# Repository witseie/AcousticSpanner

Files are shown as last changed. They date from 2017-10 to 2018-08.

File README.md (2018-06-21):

# DIY Acoustic Spanner

## Credits
* Ermes Toninelli, Mitchell A. Cox, Graham M. Gibson, Stuart D. Brown, Matthew P. Edgar, Andrew Forbes, Miles J. Padgett 
(Andrew.Forbes@wits.ac.za; Miles.Padgett@glasgow.ac.uk)

## Acknowledgements
* University of Glasgow, Scotland, United Kingdom
* University of the Witwatersrand, Johannesburg, South Africa
* EPSRC
* Centre for doctoral training in Intelligent Sensing and Measurment

## Introduction

Waves are ubiquitous in nature and we are all familiar with them: think water waves, light waves, sound waves, and so on. Everyone is familiar with the force that waves can impart on objects placed in their path. For example, a laser pointer shining on an object exerts a force on it, albeit a very small one. As it turns out, this force is directly proportional to the power of the wave and inversely proportional to its group velocity: that is, for the same power, a slower wave can exert a bigger force than a faster wave. Therefore, in the case of light waves the force is very small, as the speed of light is a very big number. Conversely, for the much slower sound waves (sound is approximately one million times slower than light) it is possible to exert a much bigger force, for an equal power expenditure.

In addition to linear momentum, both light and sound can carry orbital angular momentum (OAM). Whereas linear momentum allows one to ‘push’ objects along the direction of propagation, OAM can be used to rotate them! This form of momentum is different from the perhaps more familiar spin angular momentum, which gives rise to the phenomenon of polarisation, and it can be visualised, in the case of light, as each photon spinning on itself. When an OAM carrying field interacts with an object, it exerts a force both along the direction of propagation and around it: like the sort of force that is required to open a door, by both turning the door knob and by pushing the door.

Another example of the difference between spin angular momentum and orbital angular momentum is the Earth and Moon. The Earth rotates about it's own axis and thus has spin angular momentum. The Moon orbits around the Earth and thus has orbital angular momentum!

OAM arises from a phase structure within the field. Accordingly, many waves are used to create a certain field and the phase differences between these waves can be engineered by introducing delays, often referred to as a phased array. For example, if the waves are in phase with each other (i.e. without delays) the field can be visualised as a series of plane waves, for which the intensity of the waves is the same all over. If however, the phases are regularly changed from 0 to 2pi (one full cycle) in an azimuthal manner (going around the direction of propagation), then the field takes the form of a spiral. This is the type of field that gives rise to OAM.

In this work we use OAM carrying sound waves to build an acoustic spanner. An acoustic spanner allows to exert orbital angular momentum (OAM) on objects, causing them to rotate. Seeing this phenomenon in action is an excellent opportunity to think about the exchange of energy between sound waves and matter, and it is hence an important pedagogical tool. However, building an acoustic spanner able to spin macroscopic objects can require relatively expensive equipment and advanced technical skills. We show how to build a free-space acoustic spanner based on a 3D-printed sound-guiding structure and common electrical components. We show a video of our free-space acoustic spanner in action, in which a styrofoam packing peanut spins in a circular motion and changes direction according to the handedness of the OAM sound (see attached video).

## How do I build one?

1. You will need to get a PCB manufactured. Gerbers are provided which you can send through to your favourite manufacturer. We use Elecrow because they are cheap, fast and do a good job.
2. Accumulate all the compoments. A Bill Of Materials (BOM) is provided as a spreadsheet. The total cost is less than $100.
3. Learn to solder if you don't already know how (YouTube?). Solder all the components, carefully, to the PCB. 
4. Check your soldering and that each component is in the right place. Also check for solder bridges that shouldn't be there.
5. Burn the provided firmware to an Arduino Due using the Arduino IDE or Visual Studio Code.
6. Plug everything together and turn it on! You need to connect a 12V, 1A (or more) power supply to the top PCB for this to work.

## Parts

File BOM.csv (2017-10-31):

Qty | Value | Device | Package | Parts | Description
4 | Optional | AUDIO-JACKPTH | AUDIO-JACK | JP1 | JP2 | JP4 | JP5 | 3.5mm Audio Jack
4 |  | LED5MM | LED5MM | LED1 | LED2 | LED3 | LED4 | LED
1 | Pin Header | M03LOCK | 1X03_LOCK | JP3 | Header 3
17 | Screw Terminal | W237-102 | W237-102 | X1 | X2 | X3 | X4 | X5 | X6 | X7 | X8 | X9 | X10 | X11 | X12 | X13 | X14 | X15 | X16 | X17 | WAGO SCREW CLAMP
1 | 0.1u | C-EU025-025X050 | C025-025X050 | C27 | CAPACITOR | European symbol
10 | 1000u | CPOL-EUE5-10.5 | E5-10 | 5 | C25 | C29 | C30 | C32 | C33 | C37 | C40 | C41 | C43 | C44 | POLARIZED CAPACITOR | European symbol
11 | 100n | C-EU025-025X050 | C025-025X050 | C26 | C28 | C31 | C34 | C36 | C38 | C39 | C42 | C45 | C47 | C48 | CAPACITOR | European symbol
8 | 100nF | C-EU025-025X050 | C025-025X050 | C2 | C5 | C8 | C11 | C14 | C17 | C20 | C23 | CAPACITOR | European symbol
1 | 10k | R-EU_0207/2V | 0207/2V | R 17 | RESISTOR | European symbol
1 | 1N5400 | 1N5400 | DO201-15 | D1 | DIODE
5 | 1k | R-EU_0207/2V | 0207/2V | R 18 | R 19 | R 20 | R 21 | R 22 | RESISTOR | European symbol
16 | 270 1% | R-EU_0207/2V | 0207/2V | R 1 | R 2 | R 3 | R 4 | R 5 | R 6 | R 7 | R 8 | R 9 | R 10 | R 11 | R 12 | R 13 | R 14 | R 15 | R 16 | RESISTOR | European symbol
16 | 4.7mH 5% | L-US0207/2V | 0207/2V | L1 | L2 | L3 | L4 | L5 | L6 | L7 | L8 | L9 | L10 | L11 | L12 | L13 | L14 | L15 | L16 | INDUCTOR | American symbol
16 | 47nF | C-EU025-025X050 | C025-025X050 | C1 | C3 | C4 | C6 | C7 | C9 | C10 | C12 | C13 | C15 | C16 | C18 | C19 | C21 | C22 | C24 | CAPACITOR | European symbol
2 | 47u | CPOL-EUE2.5-5 | E2 | 05-May | C35 | C46 | POLARIZED CAPACITOR | European symbol
1 | Arduino Due | Arduino Due | Arduino Due | B1
1 | POWER_JACKSLT | POWER_JACKSLT | POWER_JACK_SLOT | JP6 | Power Jack
2 | TDA7375V | TDA7375V | MULTIWATT-15V | IC1 | IC2
1 | TOGGLE | SWITCH-MOMENTARY-2PTH | TACTILE-PTH | S1 | Various NO switches- pushbuttons | reed | etc

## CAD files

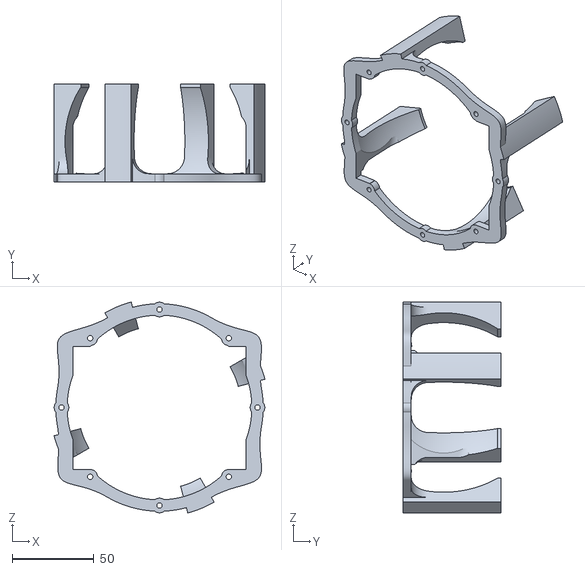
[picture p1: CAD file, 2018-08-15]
Hardware/3D printing/supportStructure.stl
129.4 x 60.0 x 129.4

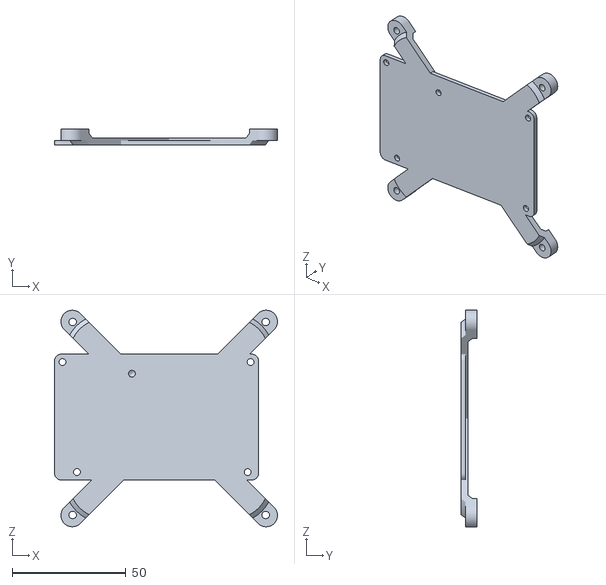
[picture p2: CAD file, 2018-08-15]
Hardware/3D printing/conesToArduinoConnectingStructure.stl
97.9 x 7.00 x 95.0

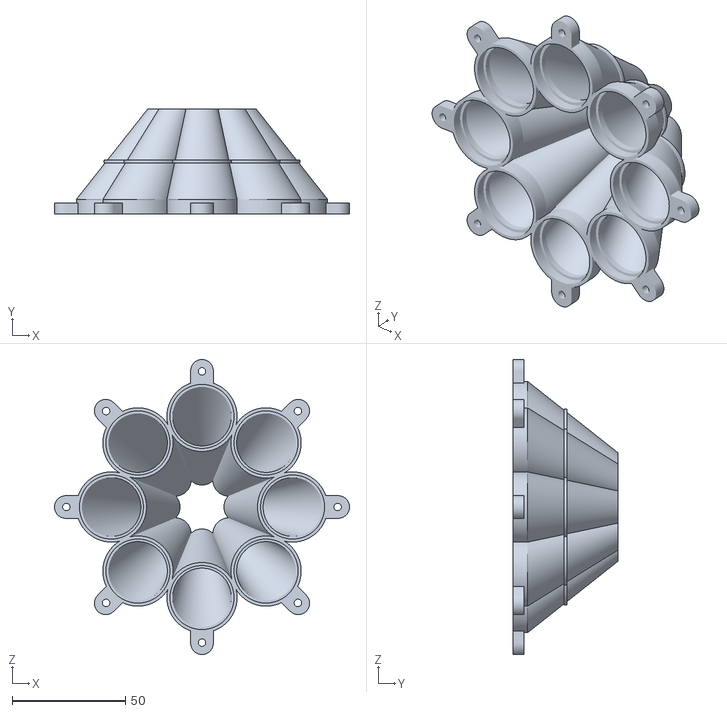
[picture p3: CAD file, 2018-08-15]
Hardware/3D printing/acousticConcentrator.stl
130.2 x 46.5 x 130.2

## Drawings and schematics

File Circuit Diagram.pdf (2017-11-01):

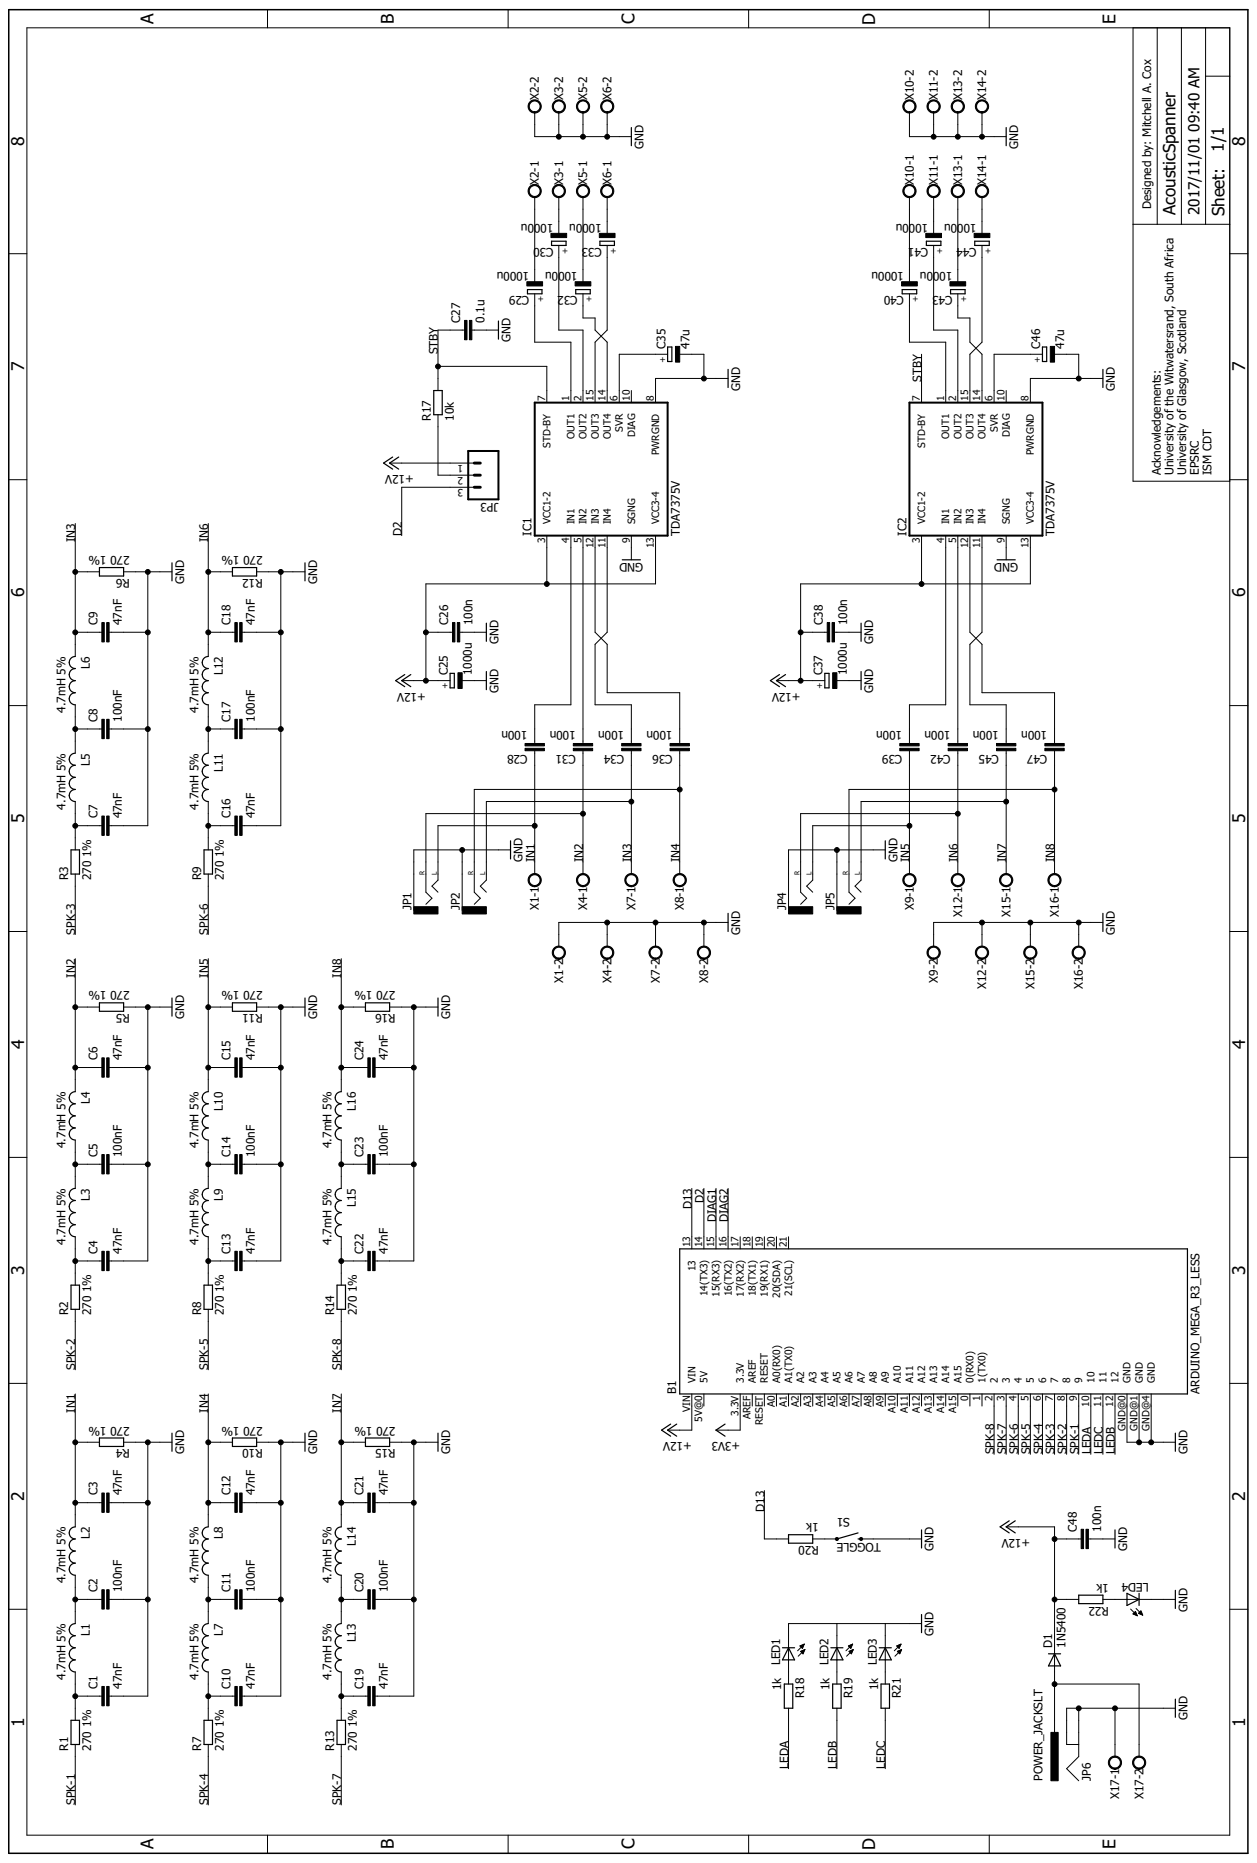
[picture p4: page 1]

Designed by: Mitchell A. Cox Acknowledgements: University of the Witwatersrand, South Africa University of Glasgow, Scotland EPSRC

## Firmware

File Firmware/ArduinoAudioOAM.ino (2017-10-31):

/*
 * ArduinoAudioOAM by Mitchell A. Cox (mitchell.cox@wits.ac.za)
 * https://github.com/witseie/ArduinoAudioOAM
 * MIT License
 * 
 * Designed to go with hardware: https://github.com/witseie/MegaSineShield
 * 
 * This code is written for the Arduino Due. 
 * 8 PWMs are used to generate sine waves pi/4 out of phase with each other.
 * When these signals are amplified and the speakers placed correctly, a
 * wavefront with orbital angular momentum is generated which can apply a
 * torque to an object.
 * 
 * Hardware Interfaces:
 * A button is present which switches the OAM \ell=+-1
 * Three LEDs present a rotation animation to represent \ell=+-1
 * 
 * 
 * References:
 * http://www.analog.com/media/en/training-seminars/tutorials/MT-085.pdf
 * http://interface.khm.de/index.php/lab/interfaces-advanced/arduino-dds-sinewave-generator/
 * 
 */

// Tweakable Parameters:
#define SINE_FREQUENCY 50 //Hz
#define NUM_OUTPUTS 8
#define OAM_l 1
#define PWM_FREQ 32812.5 //Hz (VARIANT_MCK/128/20)

#define SPK1 2
#define SPK2 3
#define SPK3 4
#define SPK4 5
#define SPK5 6
#define SPK6 7
#define SPK7 8
#define SPK8 9

#define BTN_PIN 13
#define LED1_PIN 10
#define LED2_PIN 11
#define LED3_PIN 12

#define DEBOUNCE_DELAY 50 //ms

// For the direction LEDs
#define LED_DELAY_MS 100 //ms

// Calculated / Fixed Parameters:
#define PHASE_SHIFT 2 * PI *OAM_l / NUM_OUTPUTS
#define PI_OVER_255 PI / 255

// Redefine internal Arduino stuff for analogWrite to use more than 1kHz freq.
#undef TC_FREQUENCY
#define TC_FREQUENCY PWM_FREQ
#undef PWM_FREQUENCY
#define PWM_FREQUENCY PWM_FREQ

/*
* Global Variables ------------------------------------------------------------
*/
// Lookup table for sine wave
uint8_t sine256[256];

const double refClk = PWM_FREQ;

double freq;

volatile uint8_t offset;
volatile uint32_t phaseAccum;
volatile uint32_t phaseShift[NUM_OUTPUTS];
volatile uint32_t tuningWord;

bool direction = true; //true = +, false = -

uint8_t whichLED = 1; //which LED is on (1,2 or 3)

/*
* Utility Functions -----------------------------------------------------------
*/

void startTimer(Tc *tc, uint32_t channel, IRQn_Type irq, uint32_t frequency)
{
  //See https://forum.arduino.cc/index.php?topic=130423.0
  pmc_set_writeprotect(false);
  pmc_enable_periph_clk((uint32_t)irq);
  TC_Configure(tc, channel, TC_CMR_WAVE | TC_CMR_WAVSEL_UP_RC | TC_CMR_TCCLKS_TIMER_CLOCK4);
  uint32_t rc = VARIANT_MCK / 128 / frequency; //128 because we selected TIMER_CLOCK4 above
  TC_SetRA(tc, channel, rc / 2);               //50% high, 50% low
  TC_SetRC(tc, channel, rc);
  TC_Start(tc, channel);
  tc->TC_CHANNEL[channel].TC_IER = TC_IER_CPCS;
  tc->TC_CHANNEL[channel].TC_IDR = ~TC_IER_CPCS;
  NVIC_EnableIRQ(irq);
}

void setup()
{
  Serial.begin(115200);
  Serial.println("Audio Wrench v1.0 by Mitchell A. Cox and Ermes Toninelli");

  //Set up DDS (Direct Digital Synthesis)
  freq = SINE_FREQUENCY;
  tuningWord = pow(2, 32) * freq / refClk;
  phaseAccum = 0;

  for (int i = 0; i < NUM_OUTPUTS; ++i)
  {
    phaseShift[i] = i * (pow(2, 32) / NUM_OUTPUTS);
  }

  // Populate the LUT
  double v;
  for (int i = 0; i <= 255; ++i)
  {
    v = sin((double)i * PI_OVER_255) * 255.0;
    sine256[i] = (uint8_t)v;
  }

  //Set up hardware
  pinMode(LED_BUILTIN, OUTPUT);
  pinMode(SPK1, OUTPUT);
  pinMode(SPK2, OUTPUT);
  pinMode(SPK3, OUTPUT);
  pinMode(SPK4, OUTPUT);
  pinMode(SPK5, OUTPUT);
  pinMode(SPK6, OUTPUT);
  pinMode(SPK7, OUTPUT);
  pinMode(SPK8, OUTPUT);
  pinMode(LED1_PIN, OUTPUT);
  pinMode(LED2_PIN, OUTPUT);
  pinMode(LED3_PIN, OUTPUT);
  pinMode(BTN_PIN, INPUT_PULLUP);

  //Can't use TC0 or 2 (used for PWM, etc.)
  startTimer(TC1, 0, TC3_IRQn, PWM_FREQ);
}

/*
* Work Functions --------------------------------------------------------------
*/

void loop()
{
  static uint32_t lastTick = 0;
  static int lastButtonState = LOW;
  static int buttonState = LOW;
  static uint32_t lastBounceTime = 0;

  //Do the LED rotation
  if (millis() >= (lastTick + LED_DELAY_MS))
  {
    lastTick = millis();

    //turn off existing LED
    digitalWrite(LED1_PIN + (whichLED-1), LOW);

    if (direction) {
      whichLED++;
      if (whichLED > 3) whichLED = 1;
    } else {
      whichLED--;
      if (whichLED < 1) whichLED = 3;
    }

    digitalWrite(LED1_PIN + (whichLED-1), HIGH);
  }

  //Check the button, swap direction
  //Debounce code: https://www.arduino.cc/en/Tutorial/Debounce
  int buttonReading = digitalRead(BTN_PIN);
  if (buttonReading != lastButtonState) {
    lastBounceTime = millis();
  }
  if ((millis() - lastBounceTime) >= DEBOUNCE_DELAY) {
    Serial.println("button!");
    if (buttonReading != buttonState) {
      buttonState = buttonReading;
      direction = !direction;
    }
  }

  if (Serial.available()) {
    Serial.read();
    Serial.println("Oh Hay!");
    direction = !direction;
  }
}

/*
* Interrupts ------------------------------------------------------------------
*/

void TC3_Handler() //TC1,0
{
  //Update PWM duty cycles
  TC_GetStatus(TC1, 0);

  phaseAccum += tuningWord;
  offset = (uint8_t)(phaseAccum >> 24); //divide and round down to 0-255
  analogWrite(LED_BUILTIN, sine256[offset]);

  if (direction)
  { //positive
    //offset = (uint8_t)((phaseAccum) >> 24); //phaseShift[0] = 0
    analogWrite(SPK1, sine256[offset]);
    offset = (uint8_t)((phaseAccum + phaseShift[1]) >> 24);
    analogWrite(SPK2, sine256[offset]);
    offset = (uint8_t)((phaseAccum + phaseShift[2]) >> 24);
    analogWrite(SPK3, sine256[offset]);
    offset = (uint8_t)((phaseAccum + phaseShift[3]) >> 24);
    analogWrite(SPK4, sine256[offset]);
    offset = (uint8_t)((phaseAccum + phaseShift[4]) >> 24);
    analogWrite(SPK5, sine256[offset]);
    offset = (uint8_t)((phaseAccum + phaseShift[5]) >> 24);
    analogWrite(SPK6, sine256[offset]);
    offset = (uint8_t)((phaseAccum + phaseShift[6]) >> 24);
    analogWrite(SPK7, sine256[offset]);
    offset = (uint8_t)((phaseAccum + phaseShift[7]) >> 24);
    analogWrite(SPK8, sine256[offset]);
  }
  else
  { //negative
    //offset = (uint8_t)((phaseAccum) >> 24); //phaseShift[0] = 0
    analogWrite(SPK1, sine256[offset]);
    offset = (uint8_t)((phaseAccum - phaseShift[1]) >> 24);
    analogWrite(SPK2, sine256[offset]);
    offset = (uint8_t)((phaseAccum - phaseShift[2]) >> 24);
    analogWrite(SPK3, sine256[offset]);
    offset = (uint8_t)((phaseAccum - phaseShift[3]) >> 24);
    analogWrite(SPK4, sine256[offset]);
    offset = (uint8_t)((phaseAccum - phaseShift[4]) >> 24);
    analogWrite(SPK5, sine256[offset]);
    offset = (uint8_t)((phaseAccum - phaseShift[5]) >> 24);
    analogWrite(SPK6, sine256[offset]);
    offset = (uint8_t)((phaseAccum - phaseShift[6]) >> 24);
    analogWrite(SPK7, sine256[offset]);
    offset = (uint8_t)((phaseAccum - phaseShift[7]) >> 24);
    analogWrite(SPK8, sine256[offset]);
  }
}

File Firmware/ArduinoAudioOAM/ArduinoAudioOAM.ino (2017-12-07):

/*
 * ArduinoAudioOAM by Mitchell A. Cox (mitchell.cox@wits.ac.za)
 * https://github.com/witseie/AcousticSpanner
 * MIT License
 * 
 * 
 * This code is written for the Arduino Due. 
 * 8 PWMs are used to generate sine waves pi/4 out of phase with each other.
 * When these signals are amplified and the speakers placed correctly, a
 * wavefront with orbital angular momentum is generated which can apply a
 * torque to an object.
 * 
 * Hardware Interfaces:
 * A button is present which switches the OAM \ell=+-1
 * Three LEDs present a rotation animation to represent \ell=+-1
 * 
 * 
 * References:
 * http://www.analog.com/media/en/training-seminars/tutorials/MT-085.pdf
 * http://interface.khm.de/index.php/lab/interfaces-advanced/arduino-dds-sinewave-generator/
 * 
 */

#include <Arduino.h>

// Tweakable Parameters:
#define SINE_FREQUENCY 650 //Hz
#define NUM_OUTPUTS 8
#define OAM_l 1
#define VOLUME 255.0
#define VOLUME_REDUCTION 3 //used when in phase

#define SPK1 9 //PWM
#define SPK2 8 //PWM
#define SPK3 7 //PWM
#define SPK4 6 //PWM
#define SPK5 5
#define SPK6 4
#define SPK7 3
#define SPK8 2

#define BTN_PIN 13
#define LED1_PIN 10
#define LED2_PIN 11
#define LED3_PIN 12
#define AMP_EN_PIN 14

#define DEBOUNCE_DELAY 500 //ms

// For the direction LEDs
#define LED_DELAY_MS 100 //ms

// Calculated / Fixed Parameters:
#define PI_OVER_256 PI / 256.0

// Redefine internal Arduino stuff for analogWrite to use more than 1kHz freq.
//#undef TC_FREQUENCY
//#define TC_FREQUENCY PWM_FREQ
//#undef PWM_FREQUENCY
//#define PWM_FREQUENCY PWM_FREQ
/*
* NOTE: Modify variant.h, TC_FREQUENCY and PWM_FREQUENCY must both be set to 32768 from the default 1000. 
* This file can be found at: C:\Users\youruser\AppData\Local\Arduino15\packages\arduino\hardware\sam\1.6.11\variants\arduino_due_x
*/
#define PWM_FREQ 328125 //32814 or 65626

/*
* Global Variables ------------------------------------------------------------
*/
// Lookup table for sine wave
uint16_t sine256[256];

double freq;

volatile uint8_t offset;
volatile uint32_t phaseAccum;
volatile uint32_t phaseShift[NUM_OUTPUTS];
volatile uint32_t tuningWord;

volatile bool updateSine = false;

uint8_t state = 3; //0 = +1, 1 = -1, 2 = 0, 3 = off

uint8_t whichLED = 1; //which LED is on (1,2 or 3)

/*
* Utility Functions -----------------------------------------------------------
*/

void startTimer(Tc *tc, uint32_t channel, IRQn_Type irq, uint32_t frequency)
{
  //See https://forum.arduino.cc/index.php?topic=130423.0
  pmc_set_writeprotect(false);
  pmc_enable_periph_clk((uint32_t)irq);
  TC_Configure(tc, channel, TC_CMR_WAVE | TC_CMR_WAVSEL_UP_RC | TC_CMR_TCCLKS_TIMER_CLOCK4);
  uint32_t rc = VARIANT_MCK / 128 / frequency; //128 because we selected TIMER_CLOCK4 above
  TC_SetRA(tc, channel, rc / 2);               //50% high, 50% low
  TC_SetRC(tc, channel, rc);
  TC_Start(tc, channel);
  tc->TC_CHANNEL[channel].TC_IER = TC_IER_CPCS;
  tc->TC_CHANNEL[channel].TC_IDR = ~TC_IER_CPCS;
  NVIC_EnableIRQ(irq);
}


void setup()
{
  Serial.begin(115200);
  Serial.println("Audio Wrench v1.0 by Mitchell A. Cox and Ermes Toninelli");

  //Set up DDS (Direct Digital Synthesis)
  freq = SINE_FREQUENCY;
  double refClk = PWM_FREQ/12;
  tuningWord = ((double)pow(2, 32) * (freq / refClk));
  phaseAccum = 0;
 
  for (int i = 0; i < NUM_OUTPUTS; ++i)
  {
    phaseShift[i] = i * (pow(2, 32) / NUM_OUTPUTS);
  }

  // Populate the LUT
  double v;
  for (int i = 0; i <= 255; ++i)
  {
    v = (sin((double)i * 2.0 * PI_OVER_256) + 1.0) / 2.0; //sin() is [-1,1] so shift to [0,2] and scale back to [0,1]
    v = v * VOLUME; //scale up to VOLUME
    sine256[i] = (uint16_t)v;
    //Serial.print(String(sine256[i]) + ",");
  }
  //Serial.println();
  analogWriteResolution(8);

  //Set up hardware
  pinMode(LED_BUILTIN, OUTPUT);
  pinMode(SPK1, OUTPUT);
  pinMode(SPK2, OUTPUT);
  pinMode(SPK3, OUTPUT);
  pinMode(SPK4, OUTPUT);
  pinMode(SPK5, OUTPUT);
  pinMode(SPK6, OUTPUT);
  pinMode(SPK7, OUTPUT);
  pinMode(SPK8, OUTPUT);
  pinMode(LED1_PIN, OUTPUT);
  pinMode(LED2_PIN, OUTPUT);
  pinMode(LED3_PIN, OUTPUT);
  pinMode(BTN_PIN, INPUT_PULLUP);
  pinMode(AMP_EN_PIN, OUTPUT);
  digitalWrite(AMP_EN_PIN, LOW);

  //PWM
  /*pmc_enable_periph_clk(PWM_INTERFACE_ID);
  PWMC_ConfigureClocks(PWM_FREQ*PWM_MAX_DUTY_CYCLE, 0, VARIANT_MCK);
  setupPWM(SPK1);
  setupPWM(SPK2);
  setupPWM(SPK3);
  setupPWM(SPK4); */

  //Can't use TC0 or 2 (used for PWM, etc.)
  startTimer(TC1, 0, TC3_IRQn, PWM_FREQ/12);
}

/*
* Work Functions --------------------------------------------------------------
*/

void loop()
{
  static uint32_t lastTick = 0;
  static uint32_t lastMicros = 0;
  static uint32_t nextMicros = 0;
  static int lastButtonState = LOW;
  static int buttonState = LOW;
  static uint32_t lastBounceTime = 0;

  if (updateSine) {
    UpdateSine();
    updateSine = false;
  }

  //Do the LED rotation
  if (millis() >= (lastTick + LED_DELAY_MS))
  {

    //buttonState = !buttonState;
    //digitalWrite(LED1_PIN, buttonState);
    //turn off existing LED
    digitalWrite(LED1_PIN + (whichLED-1), LOW);

    if (state == 0) {
      digitalWrite(AMP_EN_PIN, HIGH);
      whichLED++;
      if (whichLED > 3) whichLED = 1;
      digitalWrite(LED1_PIN + (whichLED-1), HIGH); 
    } else if (state == 1) {
      digitalWrite(AMP_EN_PIN, HIGH);
      whichLED--;
      if (whichLED < 1) whichLED = 3;
      digitalWrite(LED1_PIN + (whichLED-1), HIGH); 
    } else if (state == 2) {
      digitalWrite(AMP_EN_PIN, HIGH);
      digitalWrite(LED1_PIN, HIGH); 
      digitalWrite(LED2_PIN, HIGH); 
      digitalWrite(LED3_PIN, HIGH); 
    } else if (state == 3) {
      //off
      digitalWrite(AMP_EN_PIN, LOW);
      digitalWrite(LED1_PIN, LOW); 
      digitalWrite(LED2_PIN, LOW); 
      digitalWrite(LED3_PIN, LOW); 
    }

    
    lastTick = millis();
  }

  //Check the button, swap direction
  //Debounce code: https://www.arduino.cc/en/Tutorial/Debounce
  
  if (millis() >= (lastBounceTime + DEBOUNCE_DELAY)) {
    int buttonReading = digitalRead(BTN_PIN);
    if (buttonReading == LOW) {
      state++;
      if (state >= 4) state = 0;
      lastBounceTime = millis();
    }
  }

}

/*
* Interrupts ------------------------------------------------------------------
*/
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

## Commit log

2017-10-31 Added initial README, firmware and hardware files.
    [AudioWrench.brd, AudioWrench.sch]
2017-10-31 Added ISM CDT and EPSRC to the PCB
    [AudioWrench.brd]
2017-10-31 Added a rough BOM
    [BOM.csv]
2017-11-01 Renamed to Acoustic Spanner
    [AcousticSpanner.brd, AcousticSpanner.sch]
2017-11-13 Firmware updates
    [AcousticSpanner.sch]
2018-08-15 Add files via upload
    Added the source designs for Fusion360 (.f3z format) and the exported stereographic files (.stl format).
    [acousticConcentrator.stl, conesToArduinoConnectingStructure.stl, supportStructure.stl]
2018-08-15 Add files via upload
    Uploaded the videos of the 3d-printed acoustic spanner in action:
    1) graphiteFlakes.mov
    Rotational motion of macroscopic objects: rotation of graphite flakes floating on water. The circular motion of graphite flakes floating on the water surface qualitatively reveals the generated acous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
    2) packingPeanut.mov
    Rotational motion of macroscopic objects: rotation of a polystyrene packing peanut. A packing peanut is set into rotation by the intercepted OAM acoustic field.
